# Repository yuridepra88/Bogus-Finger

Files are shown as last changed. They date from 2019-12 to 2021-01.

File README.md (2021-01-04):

# Bogus-Finger
A device for realistic finger-pressing simulation

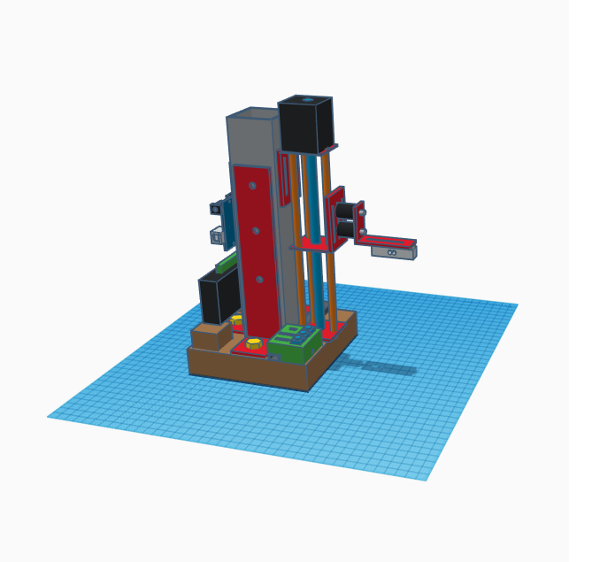
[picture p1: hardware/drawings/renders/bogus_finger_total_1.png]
Bogus Finger view


---

## Content

* Software:
	1. [Arduino](http://arduino.cc/) code for the device
  2. Python examples for direct COM control or OSC commands 

* Hardware:
	1. 3D models (made with [Tinkercad](https://www.tinkercad.com/))
	2. electronics schematics (made with [Fritzing](http://fritzing.org))
	3. list of required hardware
  4. instructions to build the device
  5. renders of the device (step-by-step construction)

---

## Licenses

The arduino code is licensed under [GNU](http://www.gnu.org/licenses/)

for everything else:  



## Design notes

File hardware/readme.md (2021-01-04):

Information about the files

- BOM.txt contains the list of the materials needed to build the Bogus Finger and some link to commercial sites where they can be found.
- The images in /drawings/renders/ will guide you in building the device. If any doubts, open /drawings/bogus_finger.stl to disassemble the 3D model. 
- fritzing project is just used as connection schema for electronics

How to build the Bogus Finger device

- screw the metal frame A (250x50x50) to the base (140x140) using 3 metal braces: 2 to the sides, one on the rear
- fix the metal frame B (12x8x140) to the base right in front of the metal vetical frame A
- screw firmly the linear stroke to the vertical metal frame A: the base of the metal stroke should contact the frame B
- fix the Arduino board and the motor contoller to base or the frame A 
- 3D print the control box and attach: the 3 buttons, the switch and the LED. Fix the control box to front-right corner and wire the buttons to the board as shown in the fritzing project.
- fix the display on the frame A and connect the 4 wires (VCC, GND, SDA, SCL)
- connect the load cell to the linear stroke through a metal brace and two M4 rubber stroke absorber
- create the control circuit (see the fritzing schema in attachment)
- attach the control circuit to the Arduino board and upload the given software
- connect the load cell and the motor driver to the control circuit

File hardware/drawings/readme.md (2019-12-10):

Some .stl file realized for 3D printed parts and block diagrams.

- bogus_finger.stl is a 3D model of the device. Many parts are just schematics to guide the user during the assembling procedures
- control_box.stl is the 3D part that hosts the buttons (to be printed)
- finger_mold.stl and mold_hat.stl are 2 pieces to print in order to mold a semi-sphere (to be placed under the load cell during the measurments)
- pcb_3x_case*.stl are containers for the PCB model 356a17 accelerometer. Contaiers may be attach to the load cell
- b&k_case.stl is a container for the 4517-C B&K accelerometer. This contaier may be attach to the load cell

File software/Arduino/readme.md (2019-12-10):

Arduino instructions

- download and add to you project the library DFRobot_LCD from https://github.com/bearwaterfall/DFRobot_LCD-master to use this LCD I2C module (https://www.dfrobot.com/product-135.html). If you are using other modules please change the LCD library and the relative code. 

- compile and upload (tested with Arduino Mega 2560)

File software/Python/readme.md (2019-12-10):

Contents:

- remote_control.py is a routine to performe a sequence of commands (i.e. incremental force steps with associated holding time) directly to the serial COM port.
- daemon_osc_bogus_finger.py is an example of OSC server mapping some of the device avalable functions to OSC commands
- osc_client_example.py is an example of OSC client that sends a routine with different pressure levels

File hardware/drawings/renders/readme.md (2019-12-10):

Some rendering of the device

Basic supports
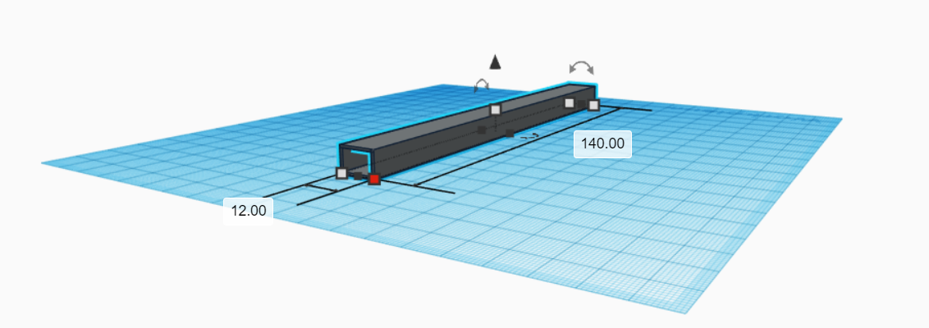
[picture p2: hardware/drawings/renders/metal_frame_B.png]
Metal frame B

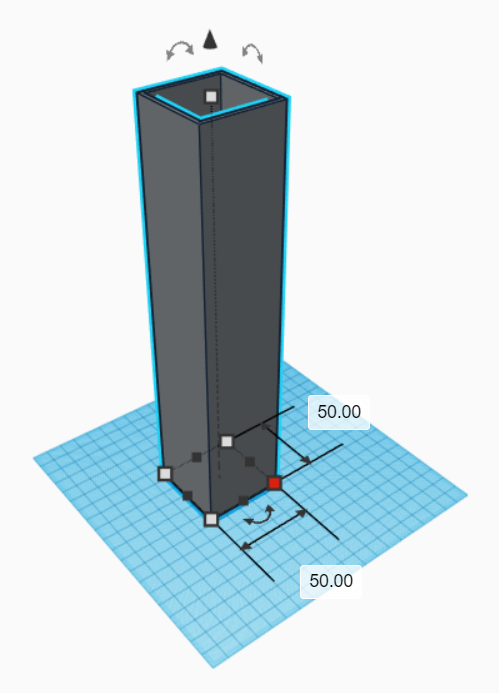
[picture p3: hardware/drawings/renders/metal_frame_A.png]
Metal frame A

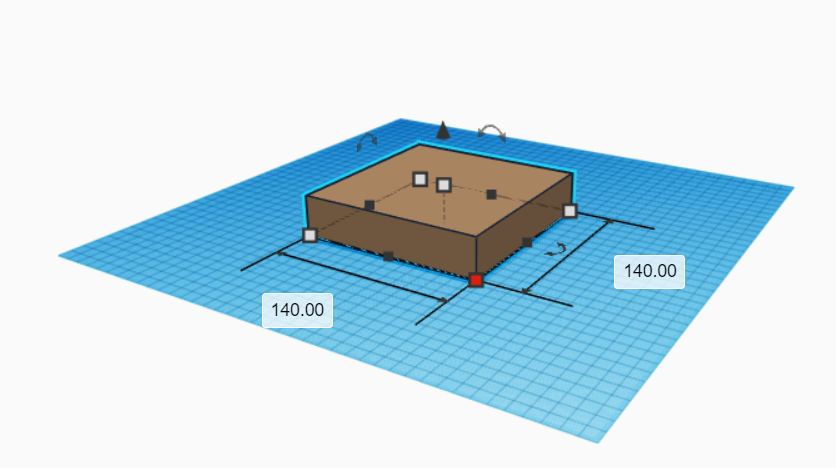
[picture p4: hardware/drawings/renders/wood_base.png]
Wood base


Supports Mounted
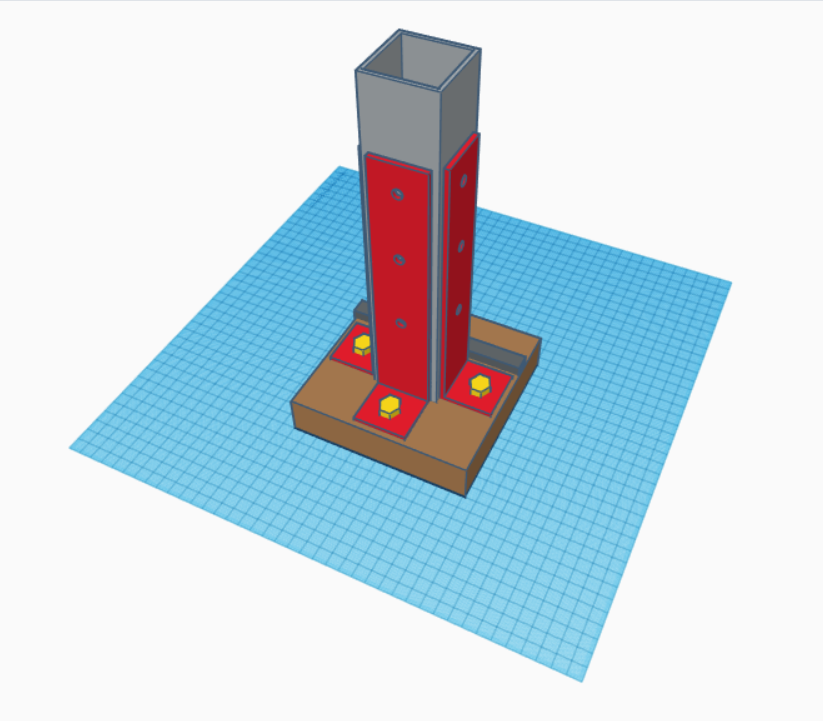
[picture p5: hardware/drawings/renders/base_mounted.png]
Base mounted


Final views
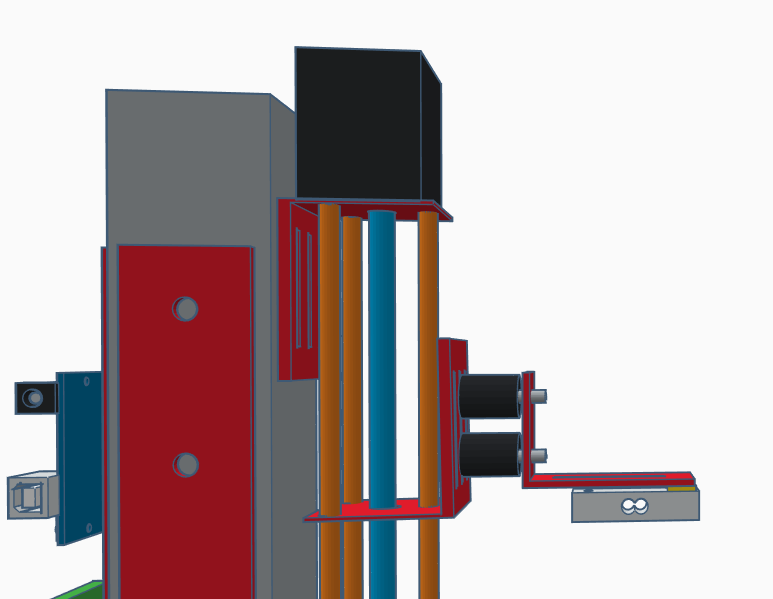
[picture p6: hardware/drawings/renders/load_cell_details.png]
Load cell Attach

Bogus Finger view 1
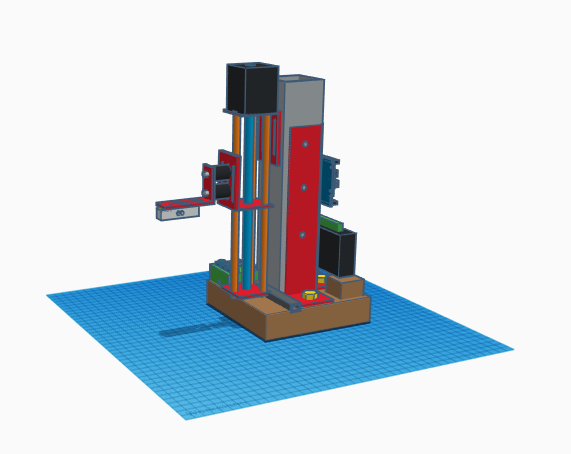
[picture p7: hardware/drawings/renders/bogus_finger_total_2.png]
Bogus Finger view 2

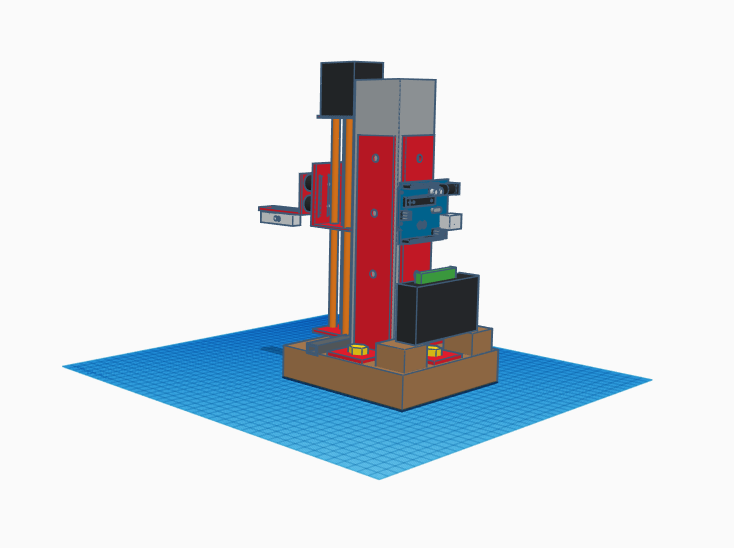
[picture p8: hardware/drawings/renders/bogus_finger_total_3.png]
Bogus Finger view 3


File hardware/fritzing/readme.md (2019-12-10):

This fritzing project summarize the connections needed. Components chosen are just placeholder for the connections (in particular the IC for the load cell)

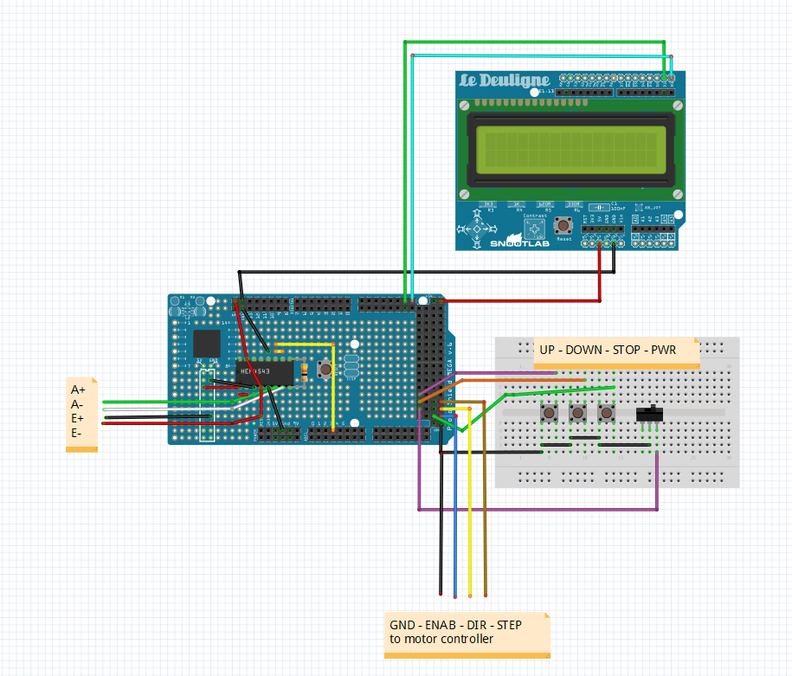
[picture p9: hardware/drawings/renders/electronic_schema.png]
Schema of cennections


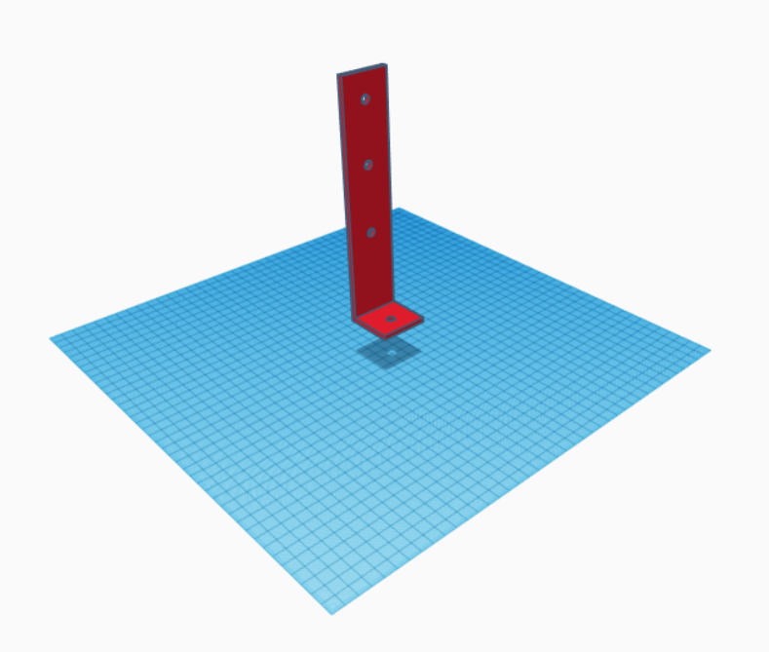
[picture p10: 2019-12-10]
hardware/drawings/renders/metal_brace.png

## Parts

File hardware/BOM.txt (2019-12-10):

List of material needed:

Pre-assembled:
- Commercial Slide-Stroke Z-Axis CNC linear actuator with at least 4 kg/cm torque (e.g. https://www.banggood.com/150mm-Slide-Stroke-Z-Axis-Mini-CNC-Linear-Motion-Milling-Engraving-Machine-p-1124302.html)
- Motor control driver for NEMA 17 motors (e.g. https://www.banggood.com/HANPOSE-TB6600-Stepper-Motor-Driver-4A-DC9-42V-For-Nema-17-or-23-or-34-Stepper-Motor-CNC-Engraving-Machine-p-1415418.html)
- Arduino Mega 2560 (for other models just change pin assignment)
- Display LCD 1602 I2C (e.g https://www.dfrobot.com/product-135.html)
- 9V 1A power supply

Electronics:
- CZL635 load cell (0-5Kg)
- INA125P amplifier
- 1 x 47ohm resistance
- 3 x push buttons
- 1 x on/off switch
- 1 x 2.5V LED (optional)

Supports:
- Solid base (wood or metal)  140x140x30
- Metal profile 50x50x250 to hold the slide stroke
- 3x metal corner braces 200x40x40 to firmly fix the metal profile to the base
- 1x metal corner brace 50x40 to hold the load cell
- 2x rubber shock absorbers M4 (e.g. https://www.alibaba.com/product-detail/2019-Amazon-hot-sale-M4-Rubber_62270287696.html)
- metal profile 12x8x140 to maintain the silde stroke vertically aligned

Custom pieces (see list of drawings for 3D printing):
- command box 
- accelerometer holders (optional)
- mold for silicon part

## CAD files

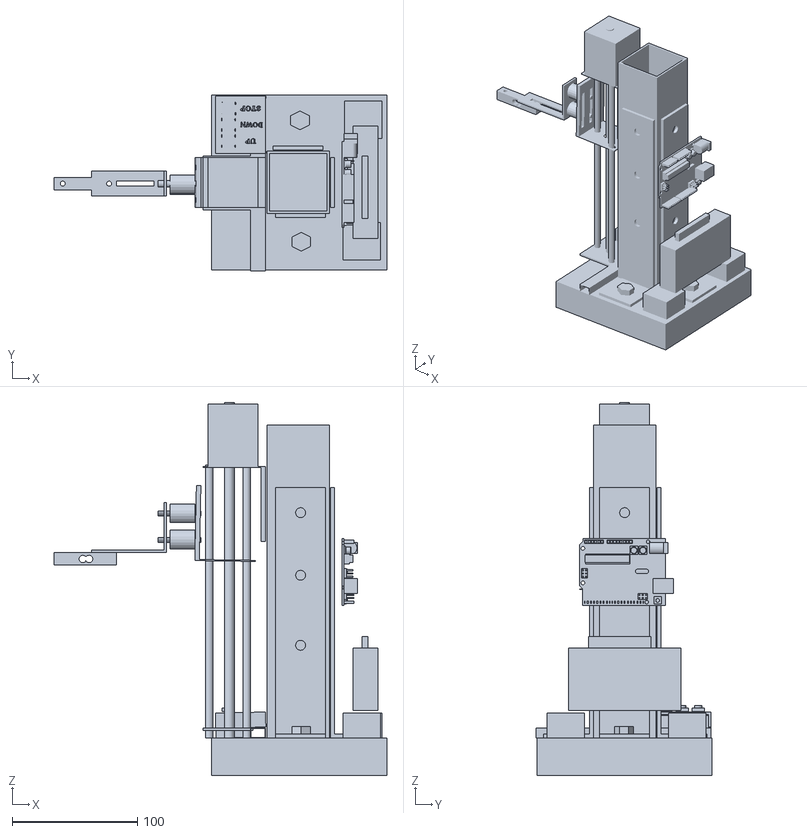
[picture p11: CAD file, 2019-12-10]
hardware/drawings/bogus_finger.stl
266.0 x 141.0 x 298.0

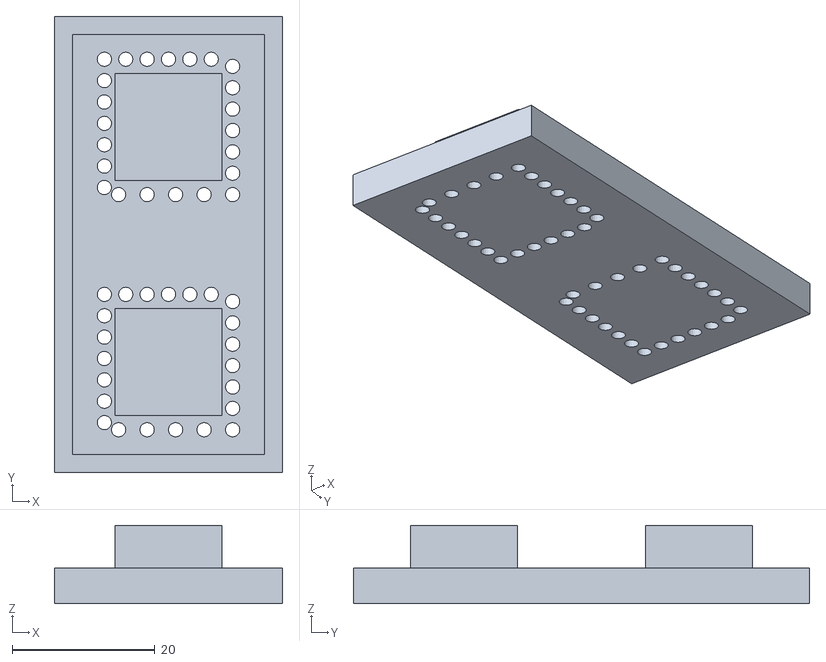
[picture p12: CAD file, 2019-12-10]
hardware/drawings/mold_hat.stl
32.0 x 64.0 x 11.0

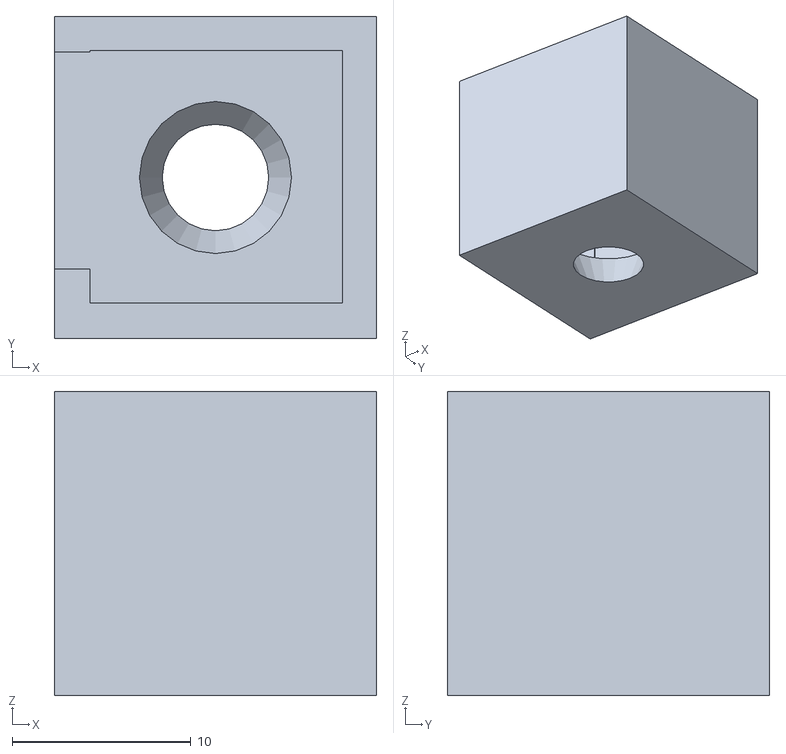
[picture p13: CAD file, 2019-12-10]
hardware/drawings/pcb_3ax_case_simple.stl
18.0 x 18.0 x 17.0

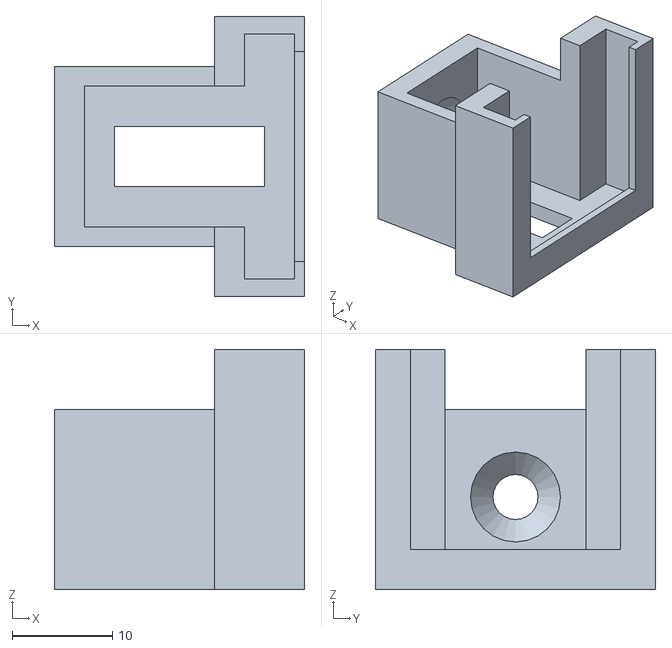
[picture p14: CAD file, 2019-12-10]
hardware/drawings/pcb_3x_case_silicon.stl
25.0 x 28.0 x 24.0

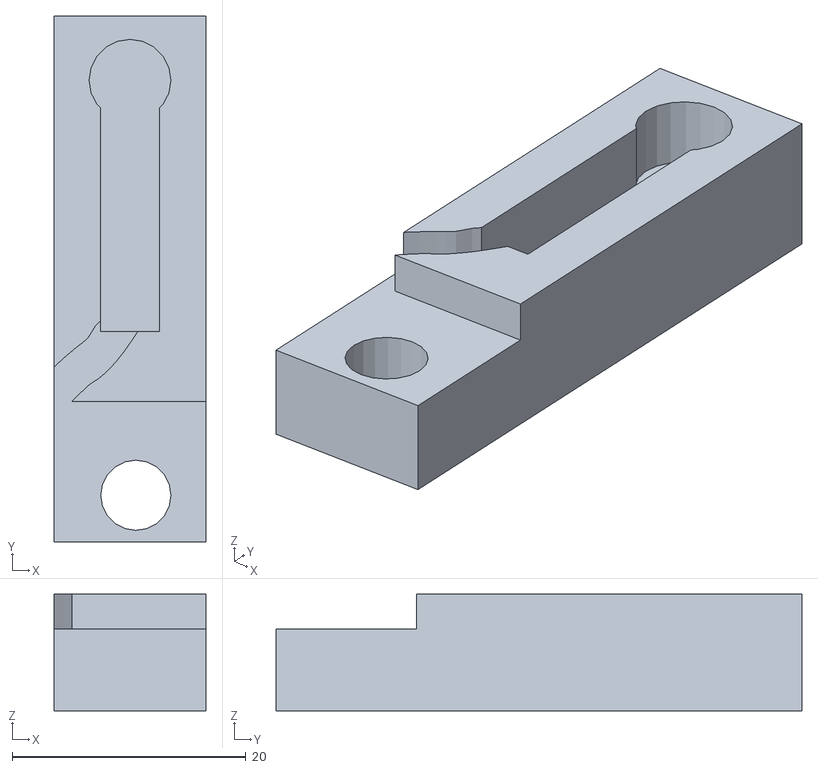
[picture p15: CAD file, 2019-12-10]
hardware/drawings/b&k_case.stl
13.0 x 45.0 x 10.0

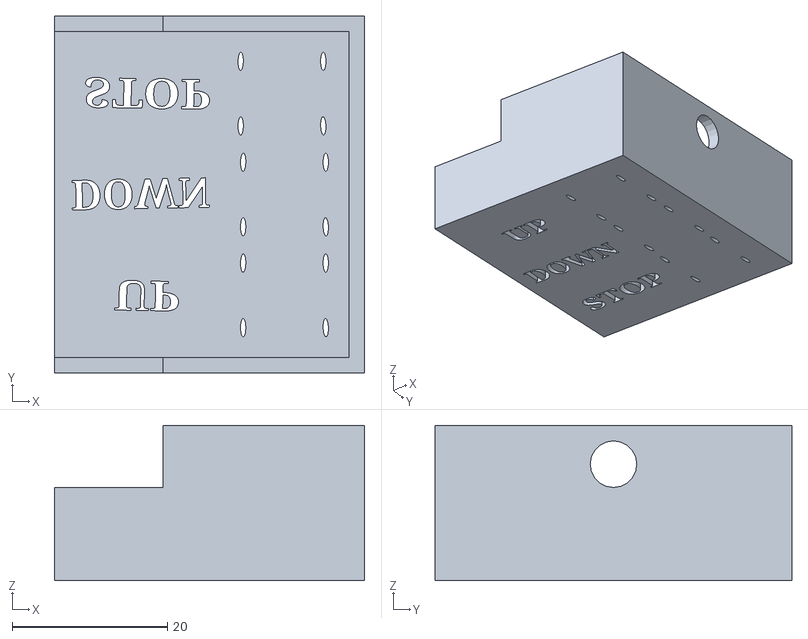
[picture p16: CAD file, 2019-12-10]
hardware/drawings/control_box.stl
40.0 x 46.0 x 20.0

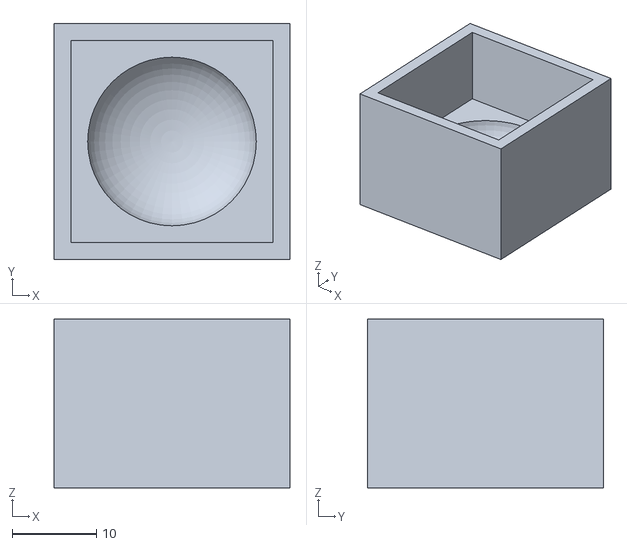
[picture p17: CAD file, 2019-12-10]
hardware/drawings/finger_mold.stl
28.0 x 28.0 x 20.0

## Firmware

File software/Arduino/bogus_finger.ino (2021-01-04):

#include <DFRobot_LCD.h>
#include <Wire.h>

/*
 * Program to control the Bogus Finger Apparatus
 * This device can be controlled with the on-board controls or through remote serial commands
 * On boards commands have higher priority
 * 
 */


const int number_func = 5;


long X=0;
long NX=0;
int MoveSpeed=600; //microseconds between steps
String     inputString = ""; // a string to hold incoming data
boolean stringComplete = true;     // whether the string is completet
boolean        ComData = false;    // whether com data is on when motors are moving will slow them down
float forceLimit = 2.0; // force in Newton to stop
boolean applyForce = false;

long maxLowPos = 110000;
long maxHighPos = 0;
  
long loadCellValue = 0;  
int offset = 17;   //16 PJR 3axis, 18 b&k 1 axes
float N = 0.00980665; // 1 gr newton conversion
float sumLc = 0;
float current_force = 0;
float output = 0;
float lc =0;
int cntprint = 0;
int btn_pwr_status = LOW;
int btn_down_status= LOW;
int btn_up_status  = LOW;
int btn_stop_status= LOW;
boolean generalStop = true;

DFRobot_LCD lcd(16,2);
int currentLCDFunction = 0; 
String lcdStringR0 = "";
String lcdStringR1 = "";
int timeRefresh = 500;
long lastRefresh = 0;
boolean functionChanged = true;
boolean standby = true;

# define X_EN_5v  53 //ENA+(+5V) stepper motor enable , active low    (yellow)
# define X_DIR_5v 51 //DIR+(+5v) axis stepper motor direction control (dark-green)
# define X_STP_5v 49 //PUL+(+5v) axis stepper motor step control      (ligh-green)
# define load_cell A4 // load cell analog port

#define BTN_STOP 52
#define BTN_DOWN 48
#define BTN_UP 46
#define BTN_PWR 50

#define LED_CHECK 47

#define F1_READ_FORCE 0
#define F2_SET_FORCE  1
#define F3_MOVE_POS   2
#define F4_MOVE_FORCE 3
#define F5_SET_ZERO   4

void setup() {

    Serial.begin(2000000);

    // MOTOR CONTROLLER SETUP  

    pinMode (X_EN_5v ,OUTPUT); //ENA+(+5V)
    pinMode (X_DIR_5v,OUTPUT); //DIR+(+5v)
    pinMode (X_STP_5v,OUTPUT); //PUL+(+5v)
    pinMode (LED_CHECK,OUTPUT);
    
    pinMode(BTN_STOP, INPUT_PULLUP);
    pinMode(BTN_DOWN, INPUT_PULLUP);
    pinMode(BTN_UP, INPUT_PULLUP);
    pinMode(BTN_PWR, INPUT_PULLUP);
    
    digitalWrite (X_EN_5v, HIGH); //ENA+(+5V) 
    digitalWrite (X_DIR_5v, LOW); //DIR+(+5v)
    digitalWrite (X_STP_5v, LOW); //PUL+(+5v)
    digitalWrite (LED_CHECK, LOW);

    // LOAD CELL SETUP
    analogReference(EXTERNAL);
    
    // LCD SETUP 
    lcd.init();
    lcd.print("Init");

}

/* Manage input serial commands */
void serialEvent()
{ while (Serial.available()) 
  {
    char inChar = (char)Serial.read();            // get the new byte
    if (inChar > 0)     {inputString += inChar;}  // add it to the inputString
    if (inChar == '\n') { stringComplete = true;} // flag command is ready 
  }
}

/* Send command description through Serial channel*/
void Help(){
 Serial.println("Commands available");
 Serial.println("check             --> verify the serial connection");
 Serial.println("on                --> turns command motor (TB6600) ON");
 Serial.println("off               --> turns command motor (TB6600) OFF");
 Serial.println("stop              --> stop current the movement");
 Serial.println("zero              --> set current position as Zero");
 Serial.println("home              --> go to zero position");
 Serial.println("getNextPos        --> return the next position set");
 Serial.println("getCurrPos        --> return the current position");
 Serial.println("getSpeed          --> return the current time in microsecond between steps");
 Serial.println("getForce          --> return the force stop set");
 Serial.println("p+Number(+/-60000)--> set the next position in steps (e.g. p10000)");
 Serial.println("f+Number(0-2000)  --> set the new force to stop in cents of Newton (e.g. f1050 --> 10.5 N)");
 Serial.println("t+Number(0-2000)  --> set Microseconds betwean steps (e.g. t500)");
 Serial.println("mp                --> motor moves to new postion");
 Serial.println("mf                --> motor moves down until it get the force set");
 Serial.println("verbose_on        --> print position data while moving");
 Serial.println("verbose_off       --> not print position data while moving");

 inputString="";
}

void CheckConnection(){
 Serial.println("cmdAck_Serial_OK");
 inputString="";
}

void ENAXON(){ 
 Serial.println("cmdAck_MOTOR_ENABLED");
 digitalWrite (X_EN_5v, LOW);
 inputString="";
}
void ENAXOFF(){  
 Serial.println("cmdAck_MOTOR_DISABLED");
 digitalWrite (X_EN_5v, HIGH);
 inputString="";
}
void SetSpeed(){
 inputString.setCharAt(0,' ');
 MoveSpeed=inputString.toInt();
 Serial.print("cmdAck_Speed=");
 Serial.println(MoveSpeed);
 inputString="";
}
void ComDataON(){
 ComData=true;
 Serial.println("cmdAck_verbose_ON");
 inputString="";
}
void ComDataOFF(){
 ComData=false;
 Serial.println("cmdAck_verbose_OFF");
 inputString="";
}
void SetNextPos(){ 
 inputString.setCharAt(0,' ');
 NX=inputString.toInt();
 Serial.print("cmdAck_Next_Position=");
 Serial.println(NX);
 inputString="";
}

void GetNextPos(){
  Serial.print("cmdAck_Next_Position=");
  Serial.println(NX);
  inputString="";
}

void GetCurrPos(){
  Serial.print("cmdAck_Current_Position=");
  Serial.println(X);
  inputString="";
}

void SetZero(){
  X =0;
  NX =0;
  Serial.print("cmdAck_New_Zero_Set");
  Serial.flush();
  delay(1000);
  inputString="";
}

void GetSpeed(){
  Serial.print("cmdAck_Current_Speed=");
  Serial.println(MoveSpeed);
  inputString="";
}

void SetForce(){
  inputString.setCharAt(0,' ');
  forceLimit=inputString.toInt()/100.0;
  Serial.print("cmdAck_New_Force=");
  Serial.println(forceLimit);
  inputString="";
}

void GetForce(){
  Serial.print("cmdAck_Current_Force=");
  Serial.println(forceLimit);
  inputString="";
}


void Moving(){
  generalStop = false; 
  Serial.println("Event_Move");  
}

void StopMe(){
  generalStop = true;
  Serial.println("Event_Stop"); 
}

void StopMeRemote(){
  generalStop = true;
  Serial.println("cmdAck_Stop"); 
}

boolean isMoving(){
  return !generalStop;
}

void nextLCDFunction(){
  currentLCDFunction++;
  currentLCDFunction= currentLCDFunction % number_func;
  lcd.clear();
  delay(500);
  functionChanged = true;
  Serial.println("Event_Function_changed"); 
}

/*Read loadcell value and convert in force stored in global variable "current_force"*/
void readLoadCell(){
  
  loadCellValue = analogRead(load_cell);
  loadCellValue -= offset;
  lc = map(loadCellValue, 0, (1023 - offset) , 0, 1023);
  if (lc > 2){ // it is reading some force
    for (int i=0; i<100; i++){
      loadCellValue = analogRead(load_cell);
      loadCellValue -= offset;
      lc = map(loadCellValue, 0, (1023 - offset) , 0, 1023);
      sumLc += lc;
    }
    lc = sumLc / 100;
    sumLc =0;
  }
     
  //values calculated on 3 axis accelerometer  (no support)
  if (lc < 50){
    output = 0.0057*pow(lc,3)- 0.5*pow(lc, 2) +17.467*lc + 15.67;
  }else{
    output = 3.3507*lc+ 152.58;
  }
  cntprint += 1;
  current_force = output*N;
  if (cntprint == 10){
    //Serial.println(output);
    cntprint = 0;
  } 
}




/* Move to de desired position NX*/
void MoveX(){ 
  int xt;
  if (NX>X)
  {xt=NX-X; digitalWrite (X_DIR_5v,LOW);xt=1;}
  else
  {xt=X-NX; digitalWrite (X_DIR_5v,HIGH);xt=-1;}
  Moving();
  Serial.println("cmdAck_MovePos");
  for (; X !=NX; X=X+xt)
  {     
       btn_stop_status = digitalRead(BTN_STOP);
       if ((btn_stop_status == LOW)|| (generalStop)){
        Serial.println("Event_Stop"); 
        break; 
       }
       digitalWrite (X_STP_5v, HIGH);
       delayMicroseconds (MoveSpeed);
       digitalWrite (X_STP_5v, LOW);
       delayMicroseconds (MoveSpeed);
       if (ComData==true){
        Serial.print("Event_CurrPos=");
        Serial.println(X);
       }
  }
  Serial.print("Event_Positon_Reached=");
  Serial.println(X);
  inputString="";
}

/* Move to zero position*/
void GoHome(){
  NX=0;
  MoveX();
  Serial.println("cmdAck_Home");
}


/*  Move down until you reach the forceLimit, then maintain */
void MoveForce(){ 
  digitalWrite (X_DIR_5v,LOW); // direction is down, fixed
  Moving();
  Serial.println("cmdAck_MoveForce");
  int current_speed = MoveSpeed;
  boolean isHolding = false;
  while (true) {  
    

     serialEvent(); 
     if (stringComplete){
        if (inputString=="stop\n")       {StopMeRemote();}
        inputString = ""; 
         stringComplete = false;
     }
      btn_stop_status = digitalRead(BTN_STOP);
     if ((btn_stop_status == LOW) || (generalStop)){
        Serial.println("Event_Stop");
        break; 
     }else{
       readLoadCell();
       
      //if you send the force value add a 2ms delay to avoid broken packets
      //String str = "Force_" + String(current_force);
      //Serial.println(str);
      //delay(2);
       

        
       
       if (current_force < (forceLimit*1.01)){
          if (current_force < (forceLimit*0.8)){ current_speed = 20;} 
          else{ current_speed = 200; }  
          applyForce = false;
          if (!isHolding){
              applyForce = true;
          }else{
            if (current_force < (forceLimit*0.99)){
              applyForce = true;
            }  
          }
          if (applyForce){
              digitalWrite (X_STP_5v, HIGH);
              delayMicroseconds (current_speed);
              digitalWrite (X_STP_5v, LOW);
              delayMicroseconds (current_speed);
              isHolding = false;    
              X = X+1;
          }
       }else{
          // force applied, start to hold 
          if (!isHolding){
            Serial.println("Event_Hold");
          }
          isHolding = true;
       }
     }
  }
  inputString="";
}


/* UPDATE LCD SCREEN */
void updateLCD(){
  boolean displayActive = true;
  switch (currentLCDFunction) {
    case F1_READ_FORCE:
      lcdStringR0 ="READ FORCE";
      readLoadCell();
      lcdStringR1 =String(current_force, 2);
      break;
    case F2_SET_FORCE:
      lcdStringR0 ="SET FORCE";
      lcdStringR1 =String(forceLimit, 2);
      break;
    case F3_MOVE_POS:
      displayActive = false;
      lcdStringR0 ="MOVE NO CHECK!";
      lcdStringR1 ="Press UP or DOWN";
      break;
    case F4_MOVE_FORCE:
      displayActive = false;
      lcdStringR0 ="MOVE UNTIL "+String(forceLimit, 2);
      lcdStringR1 ="Press DOWN";
      break;
    case F5_SET_ZERO:
      lcdStringR0 ="SET ZERO "+String(X);
      lcdStringR1 ="Press UP+DOWN";
      break;
  }
  if (((millis() - timeRefresh) > lastRefresh) && ((displayActive) || (functionChanged)) && !standby){
    functionChanged = false;
    lcd.setCursor(0,0);
    lcd.print(lcdStringR0);
    lcd.setCursor(0,1);
    lcd.print(lcdStringR1);
    lastRefresh = millis();
  }
}
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
